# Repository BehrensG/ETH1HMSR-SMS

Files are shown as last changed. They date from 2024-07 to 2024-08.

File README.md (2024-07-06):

<h1>ETH1HMSR-SMS</h1>

ETH1HMSR-SMS is a one-channel data acquisition card based on the HMSR-SMS chip. The communication with a PC is over Ethernet. The card supports LAN eXtensions for Instrumentation (LXI) and RAW TCP and UDP connections.

<h2>DESCRIPTION</h2>

<h3>Device Design</h3>

Key features of the design include:

<ul>
    <li><b>Dimensions</b>: 100 x 45 mm</li>
    <li><b>Power Supply</b>: Operates on a voltage range from 6.5 to 36 VDC (recommended 24 VDC) and includes reverse voltage protection.</li>
    <li><b>Isolation</b>: The HMSR-SMS chip provides isolation protection for the rest of the circuit.</li>
    <li><b>MCU</b>: The STM32H743VITx was selected because of its large internal FLASH and RAM memory, support for Ethernet, and internal 16-bit ADC.</li>
    <li><b>ADC</b>: Internal 16 bit ADC, configured in differential mode.</li>
    <li><b>Software</b>: FreeRTOS with lwip and SCPI parser library.</li>
</ul>

<p align="center">3D model rendition for PCB V1.2.</p>
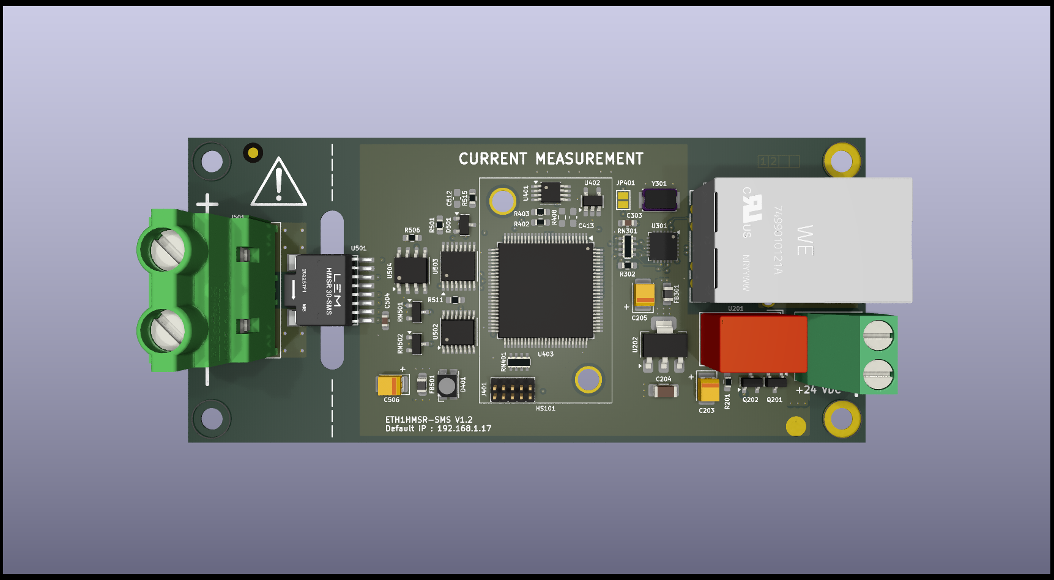
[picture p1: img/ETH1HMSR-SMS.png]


<p align="center">Below are the images for the PCB V1.0. I made some mistakes, but the botch wires fixed them.</p>

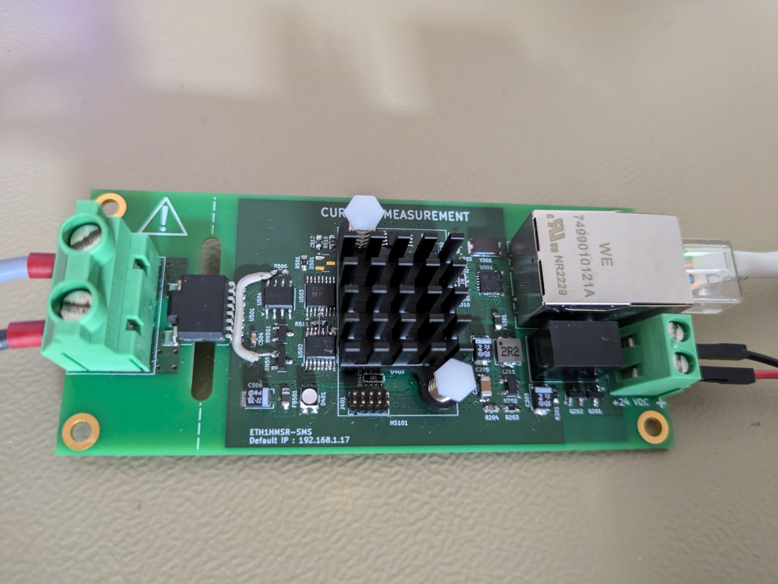
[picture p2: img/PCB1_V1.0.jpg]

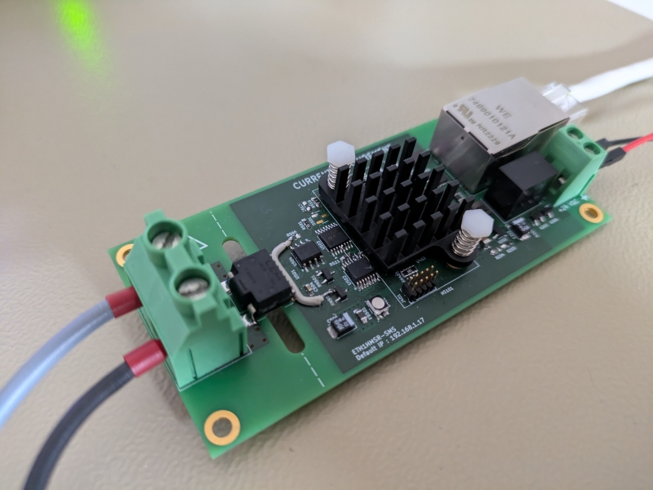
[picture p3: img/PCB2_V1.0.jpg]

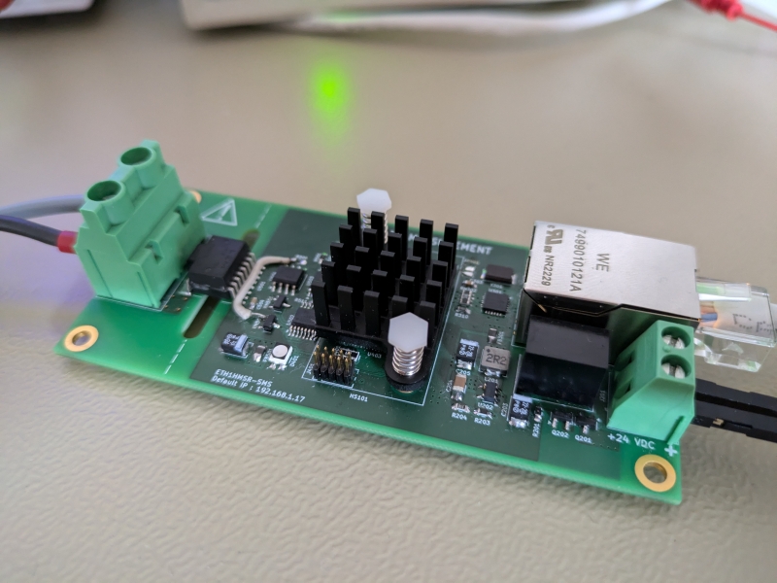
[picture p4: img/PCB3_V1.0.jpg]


<h3>Input current</h3>

The user can mount different HMSR-SMS models for different measurement ranges, those are :

<table align="center">
    <tr>
        <th>Model</th>
        <th>Nominal current (A)</th>
        <th>Measurement range (A)</th>
        <th>Supported</th>
    </tr>
    <tr>
        <td>HMSR6-SMS</td>
        <td>6</td>
        <td>+/- 15</td>
        <td><font color="green">YES</font></td>
    </tr>
    <tr>
        <td>HMSR8-SMS</td>
        <td>8</td>
        <td>+/- 20</td>
        <td><font color="green">YES</font></td>
    </tr>
    <tr>
        <td>HMSR10-SMS</td>
        <td>10</td>
        <td>+/- 25</td>
        <td><font color="green">YES</font></td>
    </tr>
    <tr>
        <td>HMSR15-SMS</td>
        <td>15</td>
        <td>+/- 37.5</td>
        <td><font color="green">YES</font></td>
    </tr>
    <tr>
        <td>HMSR20-SMS</td>
        <td>20</td>
        <td>+/- 50</td>
        <td><font color="red">NO</font></td>
    </tr>
    <tr>
        <td>HMSR30-SMS</td>
        <td>30</td>
        <td>+/- 75</td>
        <td><font color="red">NO</font></td>
    </tr>
</table>

> [!NOTE]
> The limitations is the input connector (Phoenix Contact 1710072), with nominal current of 32 A. For larger current models, the user need to redesign the PCB.

> [!NOTE]
> The prototype has a HMSR6-SMS. Other current models where not tested.

> [!TIP]
> The HMSR-SMS chip is accurate without any additional calibration.

<h2>Ethernet connection</h2>

The PCB uses Ethernet to communicate with the PC. The features are :

<h3>LAN eXtensions for Instrumentation (LXI)</h3>

LAN eXtensions for Instrumentation (LXI) is a standard for connecting and controlling test and measurement instruments via Ethernet. It allows for easy integration, remote access, and simplified configuration, enhancing the flexibility and scalability of automated test systems.

> [!WARNING]  
> This device does not guarantee full compliance with the LXI standard. The implementation was based on available documentation and observations of an LXI-compliant device.

> [!TIP]
> To use the LXI features the user needs to use a VISA API. In the examples below, the R&S VISA Tools where uses. 

<h4><p align="center">Device autodetect with multicast DNS (mDNS).</p></h4>
<hr>
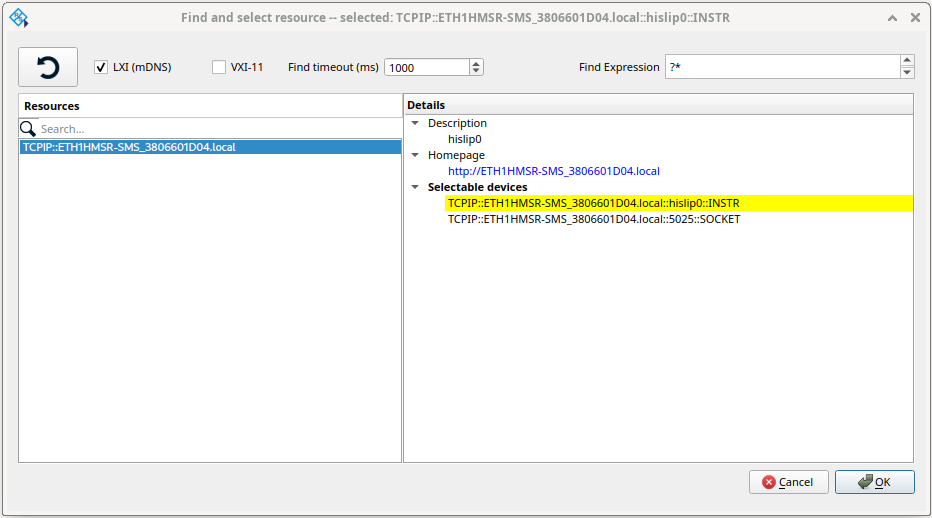
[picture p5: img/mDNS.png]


<h4><p align="center">Support for High Speed LAN Instrument Protocol (HiSLIP).</p></h4>
<hr>
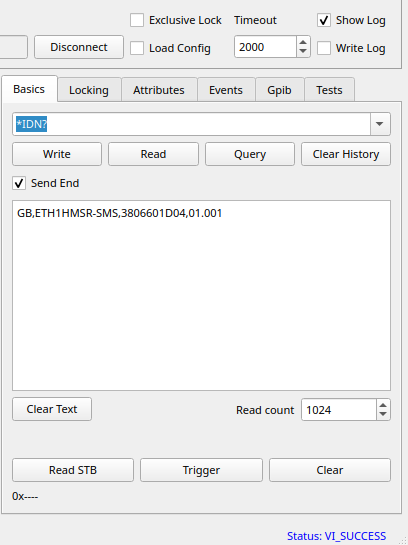
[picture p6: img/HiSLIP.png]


<h4><p align="center">Web interface</p></h4>
<hr>
The device website provides the ability to obtain device information, make measurements, and configure the device. Additionally, it offers a manual with all SCPI commands.

> [!WARNING]
> The website was tested only with Google Chrome  Browser.

<h5><p align="center">Device Home Page</p></h5>
<hr>
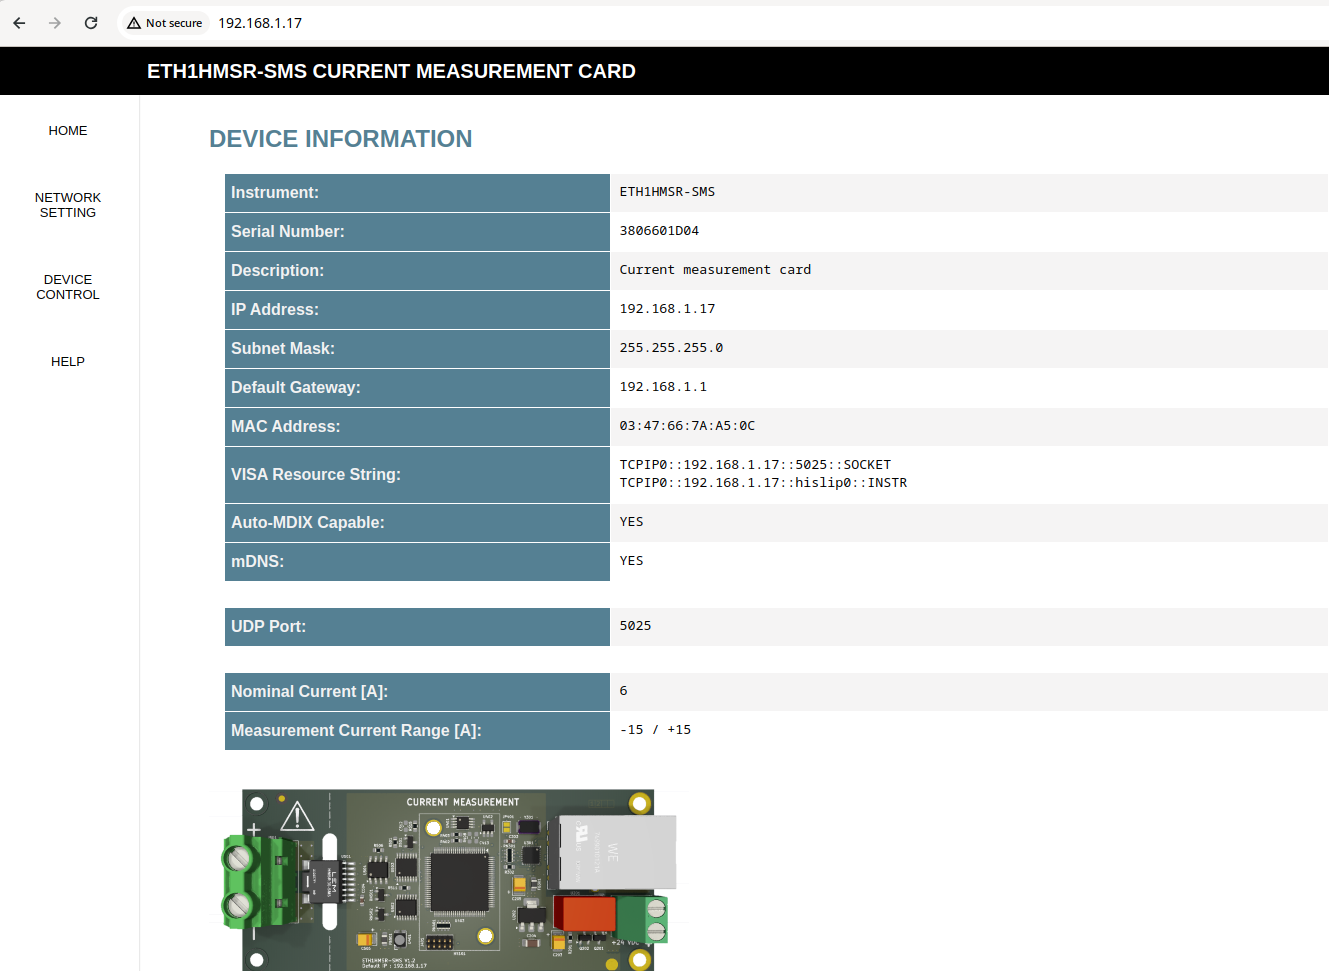
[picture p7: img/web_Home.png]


<h5><p align="center">Device Network Setup</p></h5>
<hr>
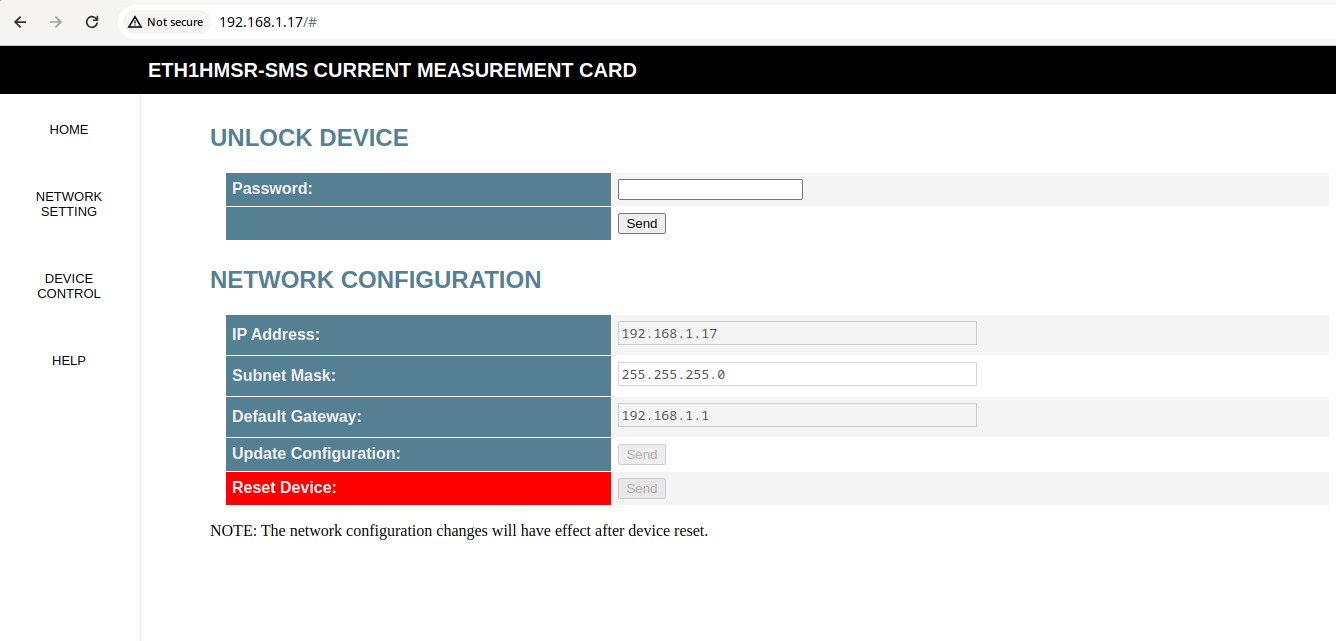
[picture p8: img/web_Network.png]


<h5><p align="center">Device Control</p></h5>
<hr>
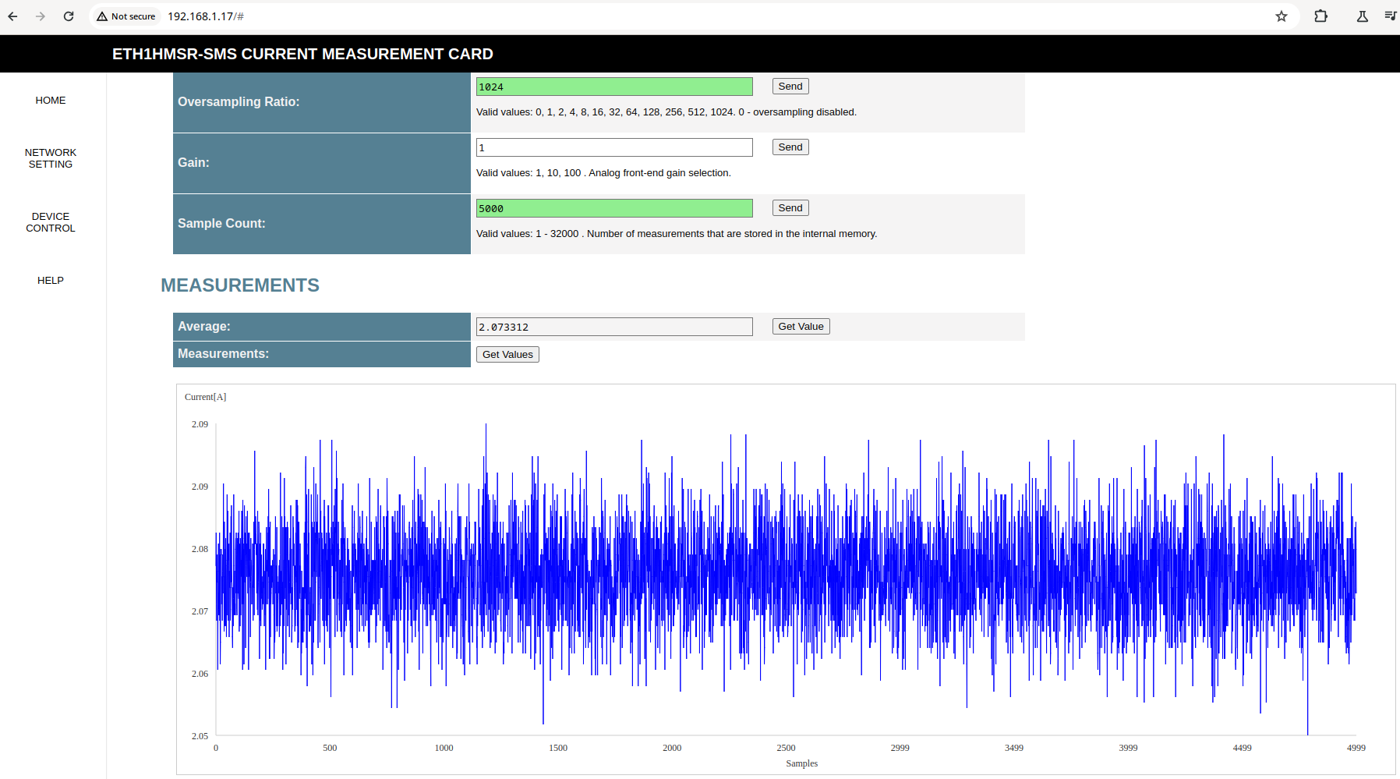
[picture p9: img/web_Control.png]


<h5><p align="center">Device Help</p></h5>
<hr>
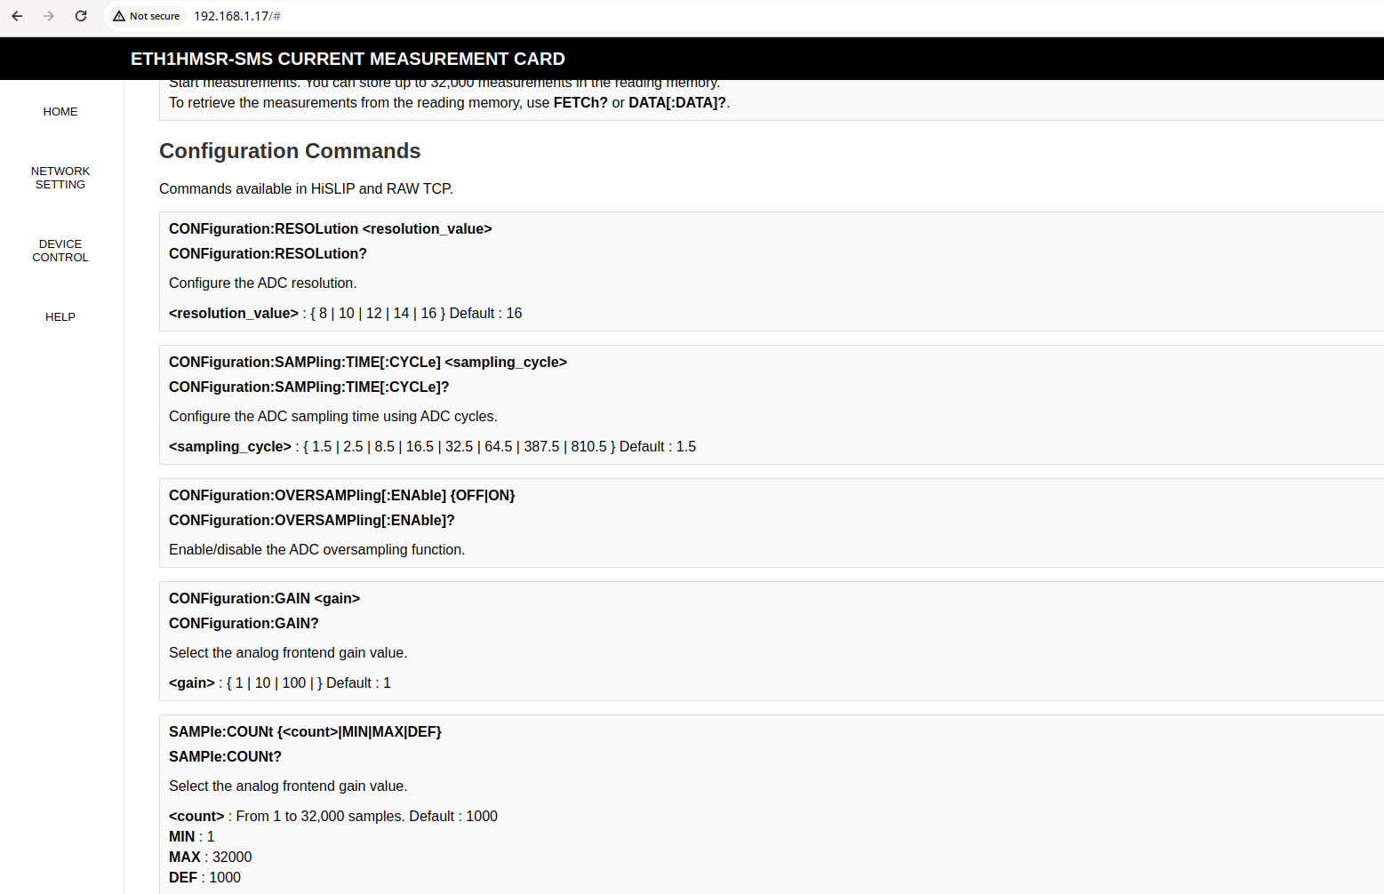
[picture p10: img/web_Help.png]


<h5><p align="center">Device Service</p></h5>
<hr>
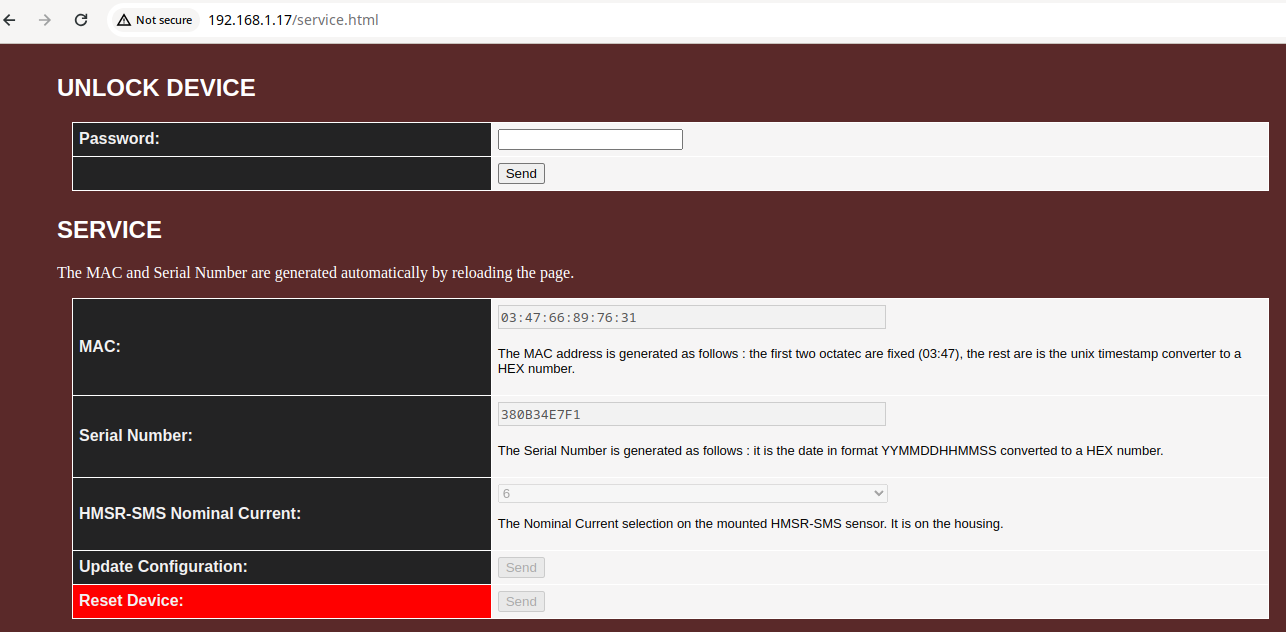
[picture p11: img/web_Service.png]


<h3>RAW TCP</h3>
The user can connect to the device directly over the TCP 5025 port.

<h5><p align="center">Using netcat</p></h5>
<hr>
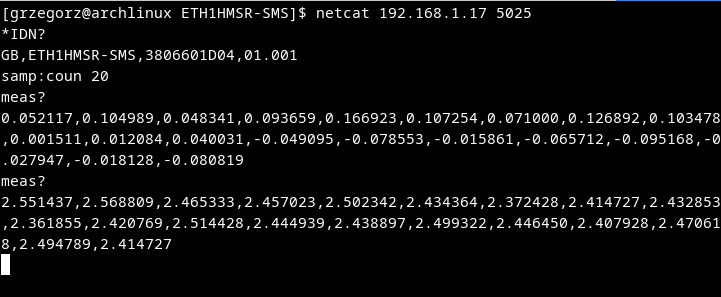
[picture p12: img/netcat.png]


<h5><p align="center">Using putty</p></h5>
<hr>
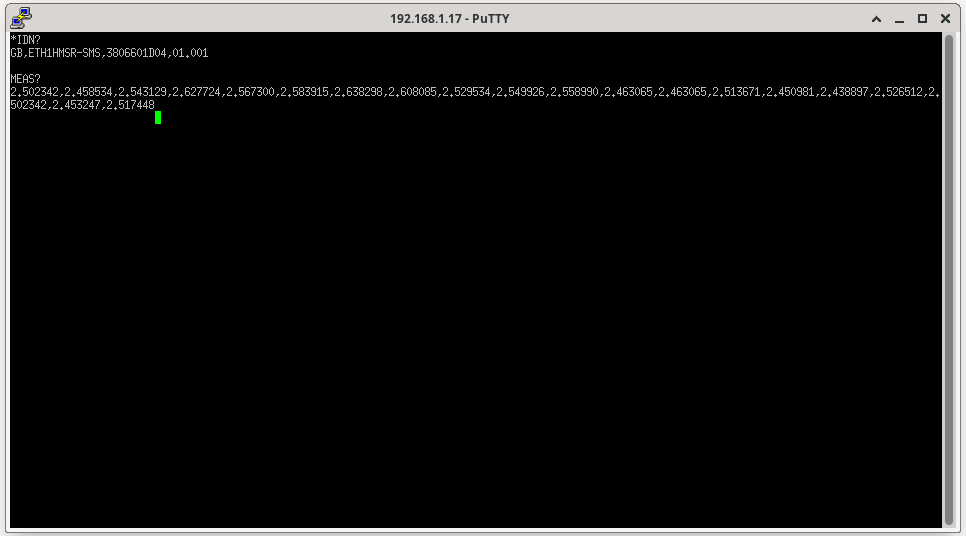
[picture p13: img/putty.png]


<h3>RAW UDP</h3>
The user can connect to the device directly via UDP port 5025. Over UDP, there is a very limited set of SCPI commands available for measurement readout.

> [!WARNING]
> The RAW UDP connection is not part of the LXI standard, it is device specific.

<h5><p align="center">Using netcat</p></h5>
<hr>
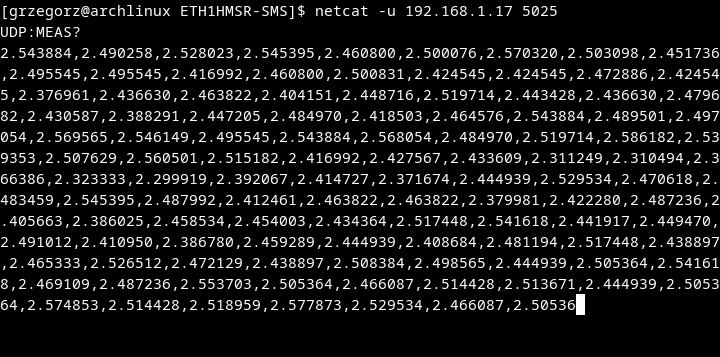
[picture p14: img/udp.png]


<h2>Links</h2>

<ul>
    <li><a href="https://www.lem.com/en/hmsr-series" target="_blank">HMSR-SMS</a></li>
    <li><a href="https://www.lxistandard.org/" target="_blank">LAN eXtensions for Instrumentation</a></li>
    <li><a href="https://www.ivifoundation.org/specifications/default.html" target="_blank">High Speed LAN Instrument Protocol (HiSLIP)</a></li>
    <li><a href="https://en.wikipedia.org/wiki/Virtual_instrument_software_architecture" target="_blank">Virtual instrument software architecture (VISA)</a></li>
    <li><a href="https://www.rohde-schwarz.com/us/driver-pages/remote-control/3-visa-and-tools_231388.html" target="_blank">R&S VISA</a></li>
    <li><a href="https://github.com/j123b567/scpi-parser" target="_blank">SCPI Parser</a></li>
   <li><a href="https://github.com/mpaland/printf" target="_blank">A printf / sprintf Implementation for Embedded Systems</a></li>
</ul>

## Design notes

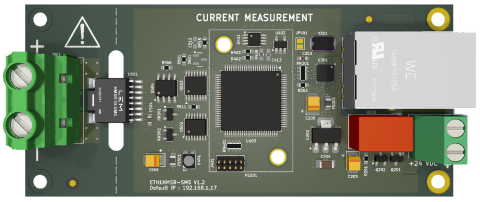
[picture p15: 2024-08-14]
SOFTWARE/ETH1HMSR-SMS/Core/BSP/HTTP/fs/img/instrument.png

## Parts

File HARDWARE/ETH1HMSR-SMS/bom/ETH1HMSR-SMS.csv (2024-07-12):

Id | Designator | Footprint | Quantity | Designation | Supplier and ref
1 | RN502,RN501 | SOT-23 | 2 | MPMT2003AT5
2 | U503 | TSSOP-16_4.4x5mm_P0.65mm | 1 | DG412LEDQ
3 | J201 | TerminalBlock_Phoenix_MKDS-1,5-2_1x02_P5.00mm_Horizontal | 1 | 1715721
4 | FB301,FB501,FB401 | L_0805_2012Metric_Pad1.05x1.20mm_HandSolder | 3 | 742792031
5 | D401 | LED_Avago_PLCC4_3.2x2.8mm_CW | 1 | ASMB-MTB1-0B3A2
6 | RN401 | R_Array_Concave_4x0603 | 1 | EXB-V8V102JV
7 | C204 | C_1206_3216Metric_Pad1.33x1.80mm_HandSolder | 1 | 10u
8 | J301 | RJ45_Wuerth_7499010121A_Horizontal | 1 | RJ45_Wuerth_7499010121A
9 | Q201 | SOT-23 | 1 | SI5618A
10 | C504,C503,C403,C505,C308,C410,C401,C501,C508,C409,C421,C407,C405,C502,C406,C312,C411,C507,C311,C309,C415,C404,C310,C422,C302 | C_0603_1608Metric_Pad1.08x0.95mm_HandSolder | 25 | 0.1u
11 | C506,C203,C205 | CP_EIA-3528-21_Kemet-B_Pad1.50x2.35mm_HandSolder | 3 | 22u
12 | R302 | R_0603_1608Metric_Pad0.98x0.95mm_HandSolder | 1 | 1k5
13 | U504 | SOIC-8_3.9x4.9mm_P1.27mm | 1 | DG419LEDY
14 | C303 | C_0603_1608Metric_Pad1.08x0.95mm_HandSolder | 1 | 470p
15 | Y301 | NX5032GA | 1 | NX5032GA-25
16 | J501 | 1710072 | 1 | 1710072
17 | J401 | PinHeader_2x05_P1.27mm_Vertical | 1 | 20021111-00010T4LF
18 | U403 | LQFP-100_14x14mm_P0.5mm | 1 | STM32H743VITx
19 | R403,R402,R506,R515,R405 | R_0603_1608Metric_Pad0.98x0.95mm_HandSolder | 5 | 0
20 | U301 | VQFN-24-1EP_4x4mm_P0.5mm_EP2.5x2.5mm_ThermalVias | 1 | LAN8742A
21 | U202 | SOT-223-3_TabPin2 | 1 | LM1117MP-3.3/NOPB
22 | HS101 | 960-19-12-S-AB-0 | 1 | 960-19-12-S-AB-0
23 | R201,R501,R202 | R_0603_1608Metric_Pad0.98x0.95mm_HandSolder | 3 | 100k
24 | U501 | HMSR-SMS | 1 | HMSR-SMS
25 | Q202 | SOT-23 | 1 | MMBT3904
26 | RN301 | R_Array_Concave_4x0603 | 1 | EXB-V8V330JV
27 | U401 | MSOP-8_3x3mm_P0.65mm | 1 | LT6350xMS8
28 | U402 | SOT-23-5_HandSoldering | 1 | REF2033AIDDCT
29 | R511 | R_0603_1608Metric_Pad0.98x0.95mm_HandSolder | 1 | 100k/0.1%
30 | U201 | Converter_DCDC_TRACO_TSR-1_THT | 1 | TSR_1-2450
31 | U502 | SSOP-16_3.9x4.9mm_P0.635mm | 1 | OPA4340EA
32 | C412,C305,C307,C408,C306,C414,C402 | C_0603_1608Metric_Pad1.08x0.95mm_HandSolder | 7 | 1u
33 | C201 | C_1206_3216Metric_Pad1.33x1.80mm_HandSolder | 1 | 10u/50V
34 | R407,R406 | R_0603_1608Metric_Pad0.98x0.95mm_HandSolder | 2 | 4k7
35 | C202 | C_1206_3216Metric_Pad1.33x1.80mm_HandSolder | 1 | 4u7/50V
36 | R303,R505,R502,R401,R504,R301,R404 | R_0603_1608Metric_Pad0.98x0.95mm_HandSolder | 7 | 10k
37 | C418 | C_0603_1608Metric_Pad1.08x0.95mm_HandSolder | 1 | 10u
38 | RN303 | R_Array_Concave_4x0603 | 1 | EXB-38V510JV
39 | R305,R306 | R_0603_1608Metric_Pad0.98x0.95mm_HandSolder | 2 | 560
40 | Y401 | NX5032GA | 1 | NX5032GA-16
41 | R513 | R_0603_1608Metric_Pad0.98x0.95mm_HandSolder | 1 | 18k/0.05%
42 | D202 | D_SOD-123 | 1 | 1N4148W
43 | C510,C511,C509 | C_0603_1608Metric_Pad1.08x0.95mm_HandSolder | 3 | 4n7
44 | D201 | SOT-23 | 1 | BZX84C10LT1G
45 | C416,C304,C301,C417 | C_0603_1608Metric_Pad1.08x0.95mm_HandSolder | 4 | 8p
46 | C419,C420 | C_0603_1608Metric_Pad1.08x0.95mm_HandSolder | 2 | 2u2
47 | U404 | MSOP-8_3x3mm_P0.65mm | 1 | 24LC08B-E/MS
48 | R512 | R_0603_1608Metric_Pad0.98x0.95mm_HandSolder | 1 | 180k/0.05%
49 | R514 | R_0603_1608Metric_Pad0.98x0.95mm_HandSolder | 1 | 2k/0.05%
50 | R503 | R_0603_1608Metric_Pad0.98x0.95mm_HandSolder | 1 | 30k
51 | R304 | R_0603_1608Metric_Pad0.98x0.95mm_HandSolder | 1 | 12k1
52 | RN302 | R_Array_Concave_4x0603 | 1 | EXB-V8V103JV
53 | F201 | Fuse_1812_4532Metric_Pad1.30x3.40mm_HandSolder | 1 | 1812L075/33DR

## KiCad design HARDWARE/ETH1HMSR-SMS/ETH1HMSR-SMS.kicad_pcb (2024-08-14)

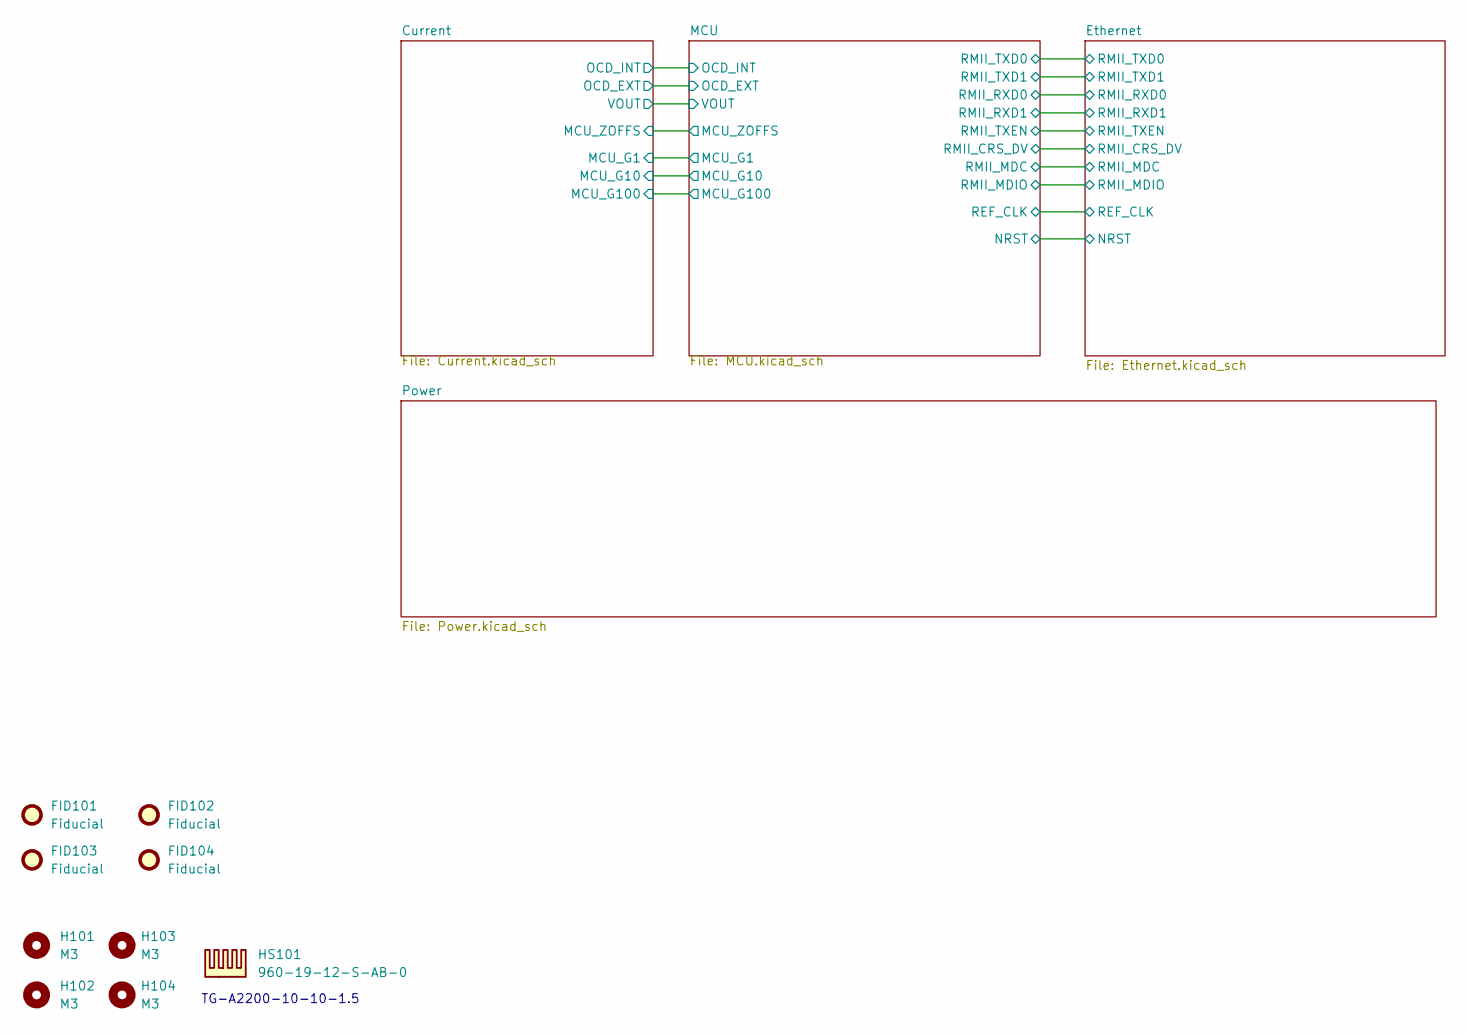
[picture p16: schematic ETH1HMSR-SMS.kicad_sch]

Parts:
FID101, FID102, FID103, FID104: Fiducial; Fiducial_1.5mm_Mask3mm
H101, H102: M3; MountingHole_3.2mm_M3_DIN965
H103, H104: M3; MountingHole_3.2mm_M3_DIN965_Pad
HS101: 960-19-12-S-AB-0

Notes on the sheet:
TG-A2200-10-10-1.5

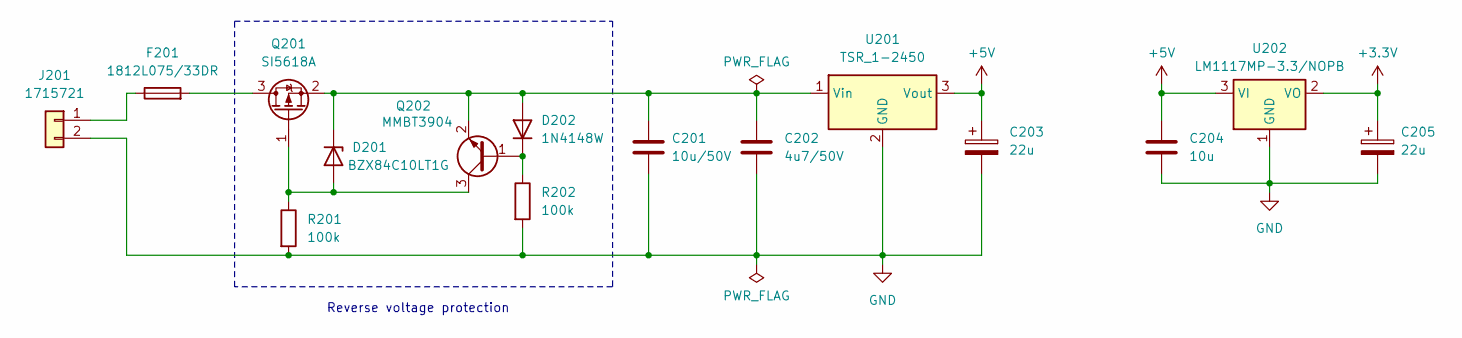
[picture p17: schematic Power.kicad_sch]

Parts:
C201: 10u/50V; C_1206_3216Metric_Pad1.33x1.80mm_HandSolder
C202: 4u7/50V; C_1206_3216Metric_Pad1.33x1.80mm_HandSolder
C203, C205: 22u; CP_EIA-3528-21_Kemet-B_Pad1.50x2.35mm_HandSolder
C204: 10u; C_1206_3216Metric_Pad1.33x1.80mm_HandSolder
D201: BZX84C10LT1G; SOT-23
D202: 1N4148W; D_SOD-123
F201: 1812L075/33DR; Fuse_1812_4532Metric_Pad1.30x3.40mm_HandSolder
J201: 1715721; TerminalBlock_Phoenix_MKDS-1,5-2_1x02_P5.00mm_Horizontal
Q201: SI5618A; SOT-23
Q202: MMBT3904; SOT-23
R201, R202: 100k; R_0603_1608Metric_Pad0.98x0.95mm_HandSolder
U201: TSR_1-2450; Converter_DCDC_TRACO_TSR-1_THT
U202: LM1117MP-3.3/NOPB; SOT-223-3_TabPin2

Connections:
+3.3V: C205.1, U202.2 (VO); also elsewhere on the board
+5V: C203.1, C204.1, U201.3 (Vout), U202.3 (VI); also elsewhere on the board
GND: C201.2, C202.2, C203.2, C204.2, C205.2, J201.2, R201.2, R202.2, U201.2 (GND), U202.1 (GND); also elsewhere on the board
unnamed: D201.1 (A), Q201.1 (G), Q202.3 (C), R201.1
unnamed: C201.1, C202.1, D201.3 (K), D202.2 (A), Q201.2 (S), Q202.2 (E), U201.1 (Vin)
unnamed: D202.1 (K), Q202.1 (B), R202.1
unnamed: F201.1, J201.1
unnamed: F201.2, Q201.3 (D)

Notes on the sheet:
Reverse voltage protection

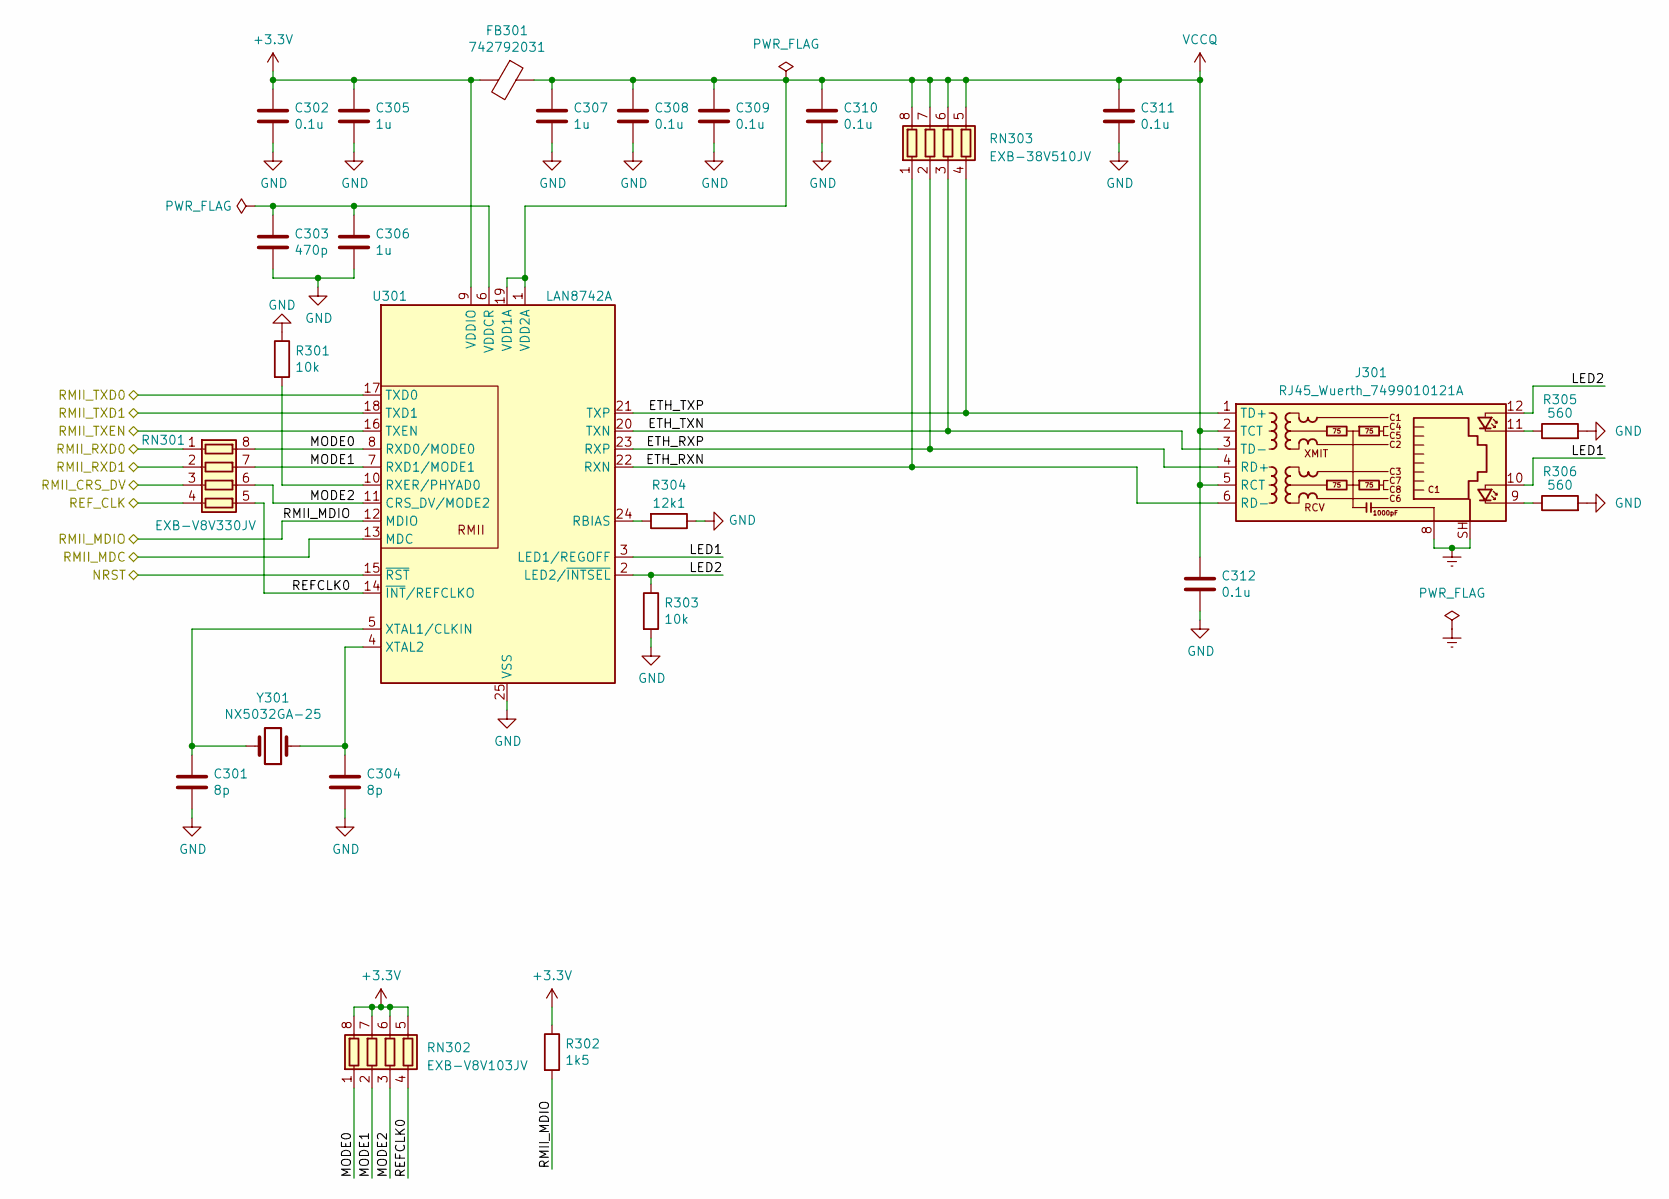
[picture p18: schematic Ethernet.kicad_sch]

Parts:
C301, C304: 8p; C_0603_1608Metric_Pad1.08x0.95mm_HandSolder
C302, C308, C309, C310, C311, C312: 0.1u; C_0603_1608Metric_Pad1.08x0.95mm_HandSolder
C303: 470p; C_0603_1608Metric_Pad1.08x0.95mm_HandSolder
C305, C306, C307: 1u; C_0603_1608Metric_Pad1.08x0.95mm_HandSolder
FB301: 742792031; L_0805_2012Metric_Pad1.05x1.20mm_HandSolder
J301: RJ45_Wuerth_7499010121A; RJ45_Wuerth_7499010121A_Horizontal
R301, R303: 10k; R_0603_1608Metric_Pad0.98x0.95mm_HandSolder
R302: 1k5; R_0603_1608Metric_Pad0.98x0.95mm_HandSolder
R304: 12k1; R_0603_1608Metric_Pad0.98x0.95mm_HandSolder
R305, R306: 560; R_0603_1608Metric_Pad0.98x0.95mm_HandSolder
RN301: EXB-V8V330JV; R_Array_Concave_4x0603
RN302: EXB-V8V103JV; R_Array_Concave_4x0603
RN303: EXB-38V510JV; R_Array_Concave_4x0603
U301: LAN8742A; VQFN-24-1EP_4x4mm_P0.5mm_EP2.5x2.5mm_ThermalVias
Y301: NX5032GA-25; NX5032GA

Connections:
+3.3V: C302.1, C305.1, FB301.2, R302.1, RN302.5 (R4.2), RN302.6 (R3.2), RN302.7 (R2.2), RN302.8 (R1.2), U301.9 (VDDIO); also elsewhere on the board
/Ethernet/ETH_RXN: J301.6 (RD-), RN303.1 (R1.1), U301.22 (RXN)
/Ethernet/ETH_RXP: J301.4 (RD+), RN303.2 (R2.1), U301.23 (RXP)
/Ethernet/ETH_TXN: J301.3 (TD-), RN303.3 (R3.1), U301.20 (TXN)
/Ethernet/ETH_TXP: J301.1 (TD+), RN303.4 (R4.1), U301.21 (TXP)
/Ethernet/LED1: J301.10, U301.3 (LED1/REGOFF)
/Ethernet/LED2: J301.12, R303.1, U301.2 (LED2/~INTSEL)
/Ethernet/MODE0: RN301.8 (R1.2), RN302.1 (R1.1), U301.8 (RXD0/MODE0)
/Ethernet/MODE1: RN301.7 (R2.2), RN302.2 (R2.1), U301.7 (RXD1/MODE1)
/Ethernet/MODE2: RN301.6 (R3.2), RN302.3 (R3.1), U301.11 (CRS_DV/MODE2)
/Ethernet/REFCLK0: RN301.5 (R4.2), RN302.4 (R4.1), U301.14 (~INT/REFCLKO)
/Ethernet/REF_CLK: RN301.4 (R4.1); also elsewhere on the board
/Ethernet/RMII_CRS_DV: RN301.3 (R3.1); also elsewhere on the board
/Ethernet/RMII_MDC: U301.13 (MDC); also elsewhere on the board
/Ethernet/RMII_MDIO: R302.2, U301.12 (MDIO); also elsewhere on the board
/Ethernet/RMII_RXD0: RN301.1 (R1.1); also elsewhere on the board
/Ethernet/RMII_RXD1: RN301.2 (R2.1); also elsewhere on the board
/Ethernet/RMII_TXD0: U301.17 (TXD0); also elsewhere on the board
/Ethernet/RMII_TXD1: U301.18 (TXD1); also elsewhere on the board
/Ethernet/RMII_TXEN: U301.16 (TXEN); also elsewhere on the board
/MCU/NRST: U301.15 (~RST); also elsewhere on the board
Earth: J301.8, J301.SH
GND: C301.2, C302.2, C303.2, C304.2, C305.2, C306.2, C307.2, C308.2, C309.2, C310.2, C311.2, C312.2, R301.1, R303.2, R304.1, R305.2, R306.2, U301.25 (VSS); also elsewhere on the board
unnamed: J301.9, R306.1
unnamed: J301.11, R305.1
unnamed: R304.2, U301.24 (RBIAS)
unnamed: R301.2, U301.10 (RXER/PHYAD0)
unnamed: C303.1, C306.1, U301.6 (VDDCR)
unnamed: C301.1, U301.5 (XTAL1/CLKIN), Y301.2
unnamed: C304.1, U301.4 (XTAL2), Y301.1
VCCQ: C307.1, C308.1, C309.1, C310.1, C311.1, C312.1, FB301.1, J301.2 (TCT), J301.5 (RCT), RN303.5 (R4.2), RN303.6 (R3.2), RN303.7 (R2.2), RN303.8 (R1.2), U301.1 (VDD2A), U301.19 (VDD1A)

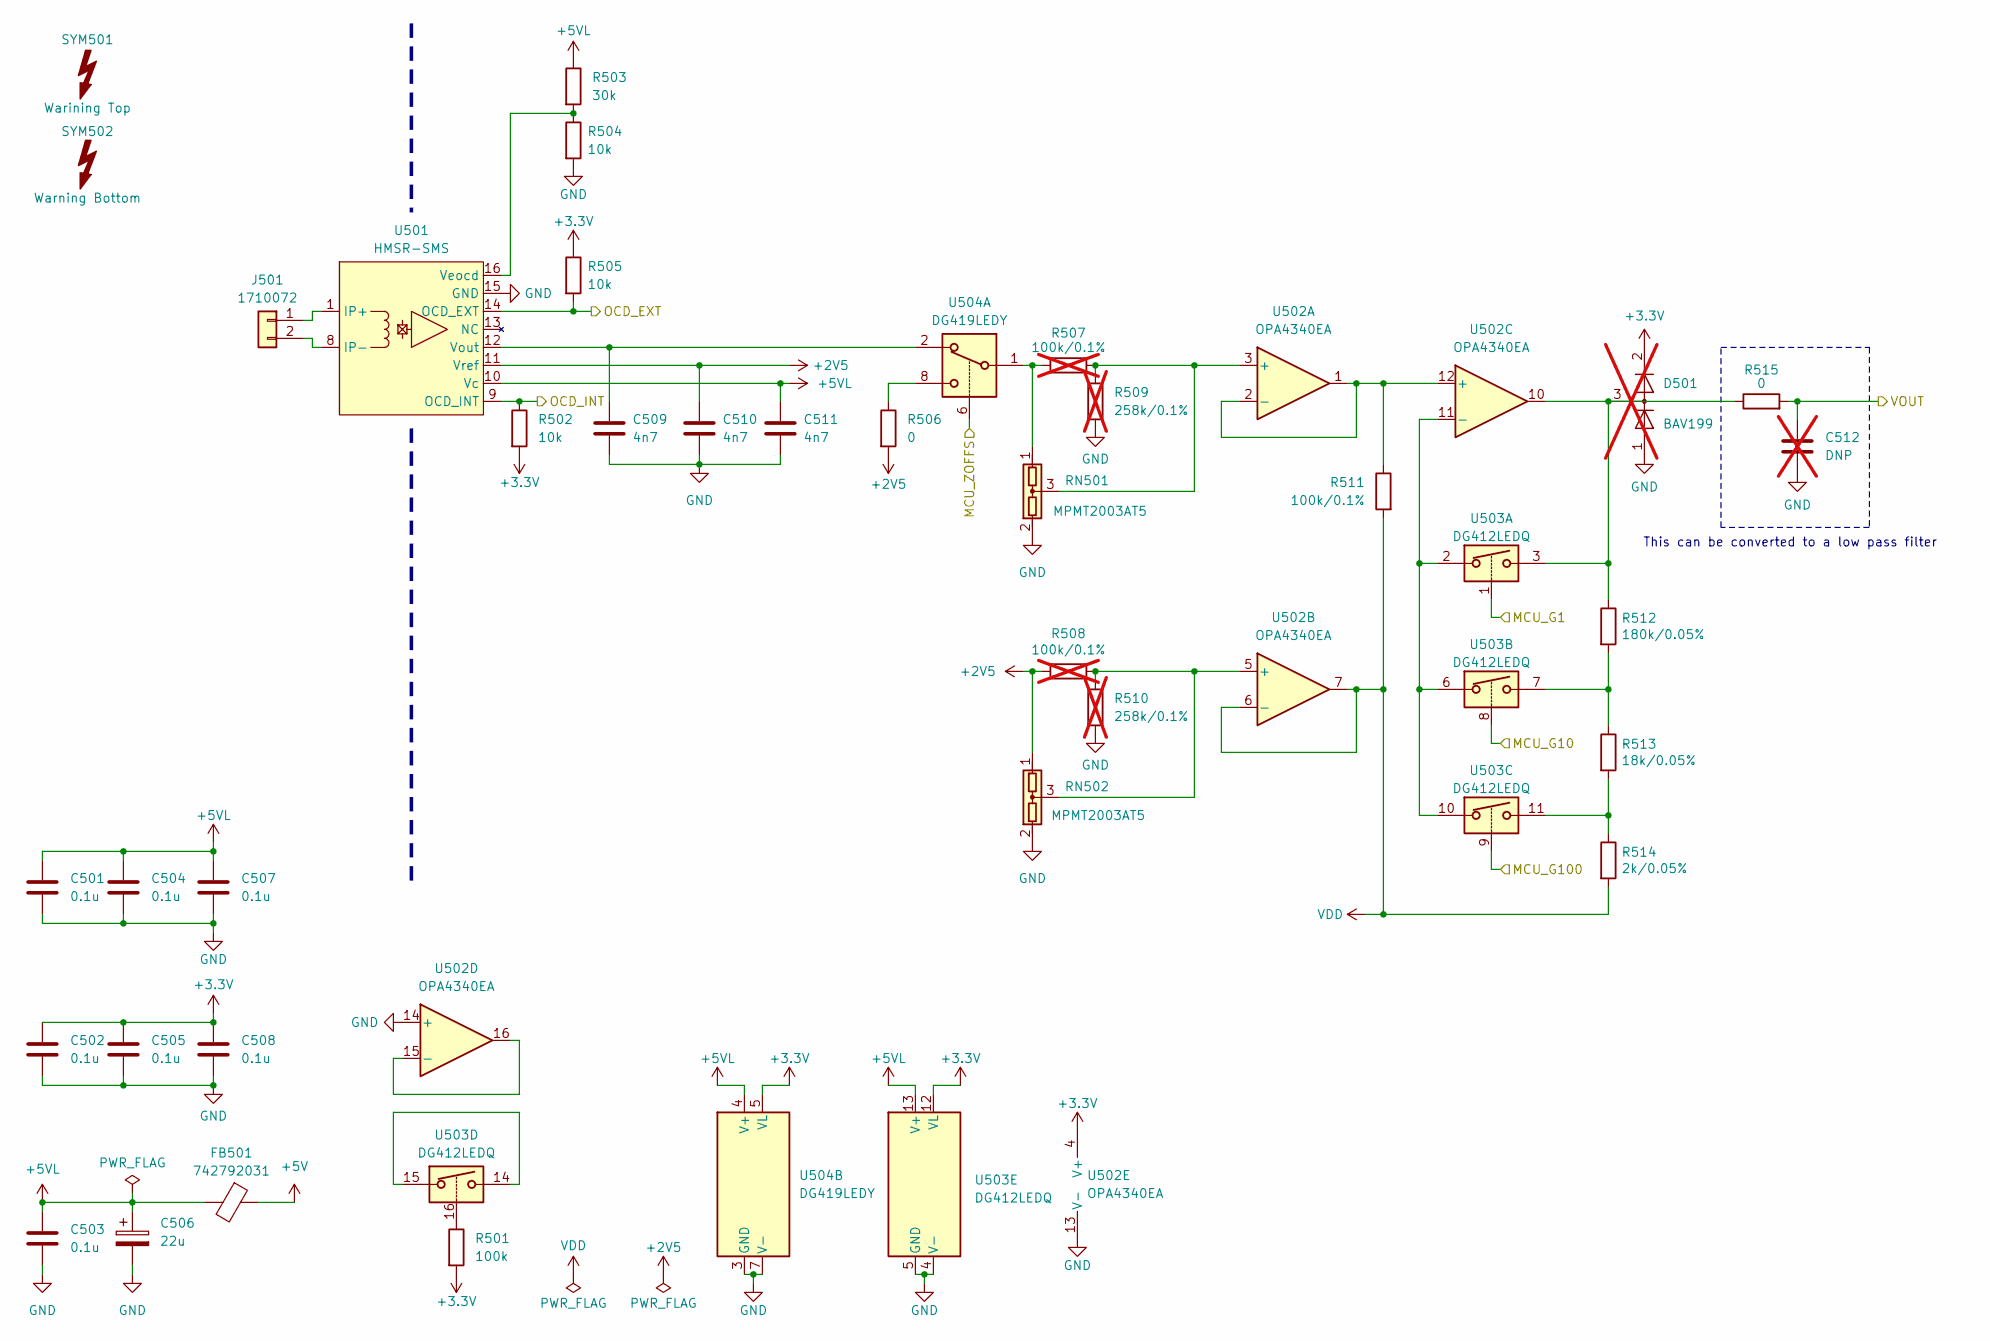
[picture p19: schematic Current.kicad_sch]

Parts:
C501, C502, C503, C504, C505, C507, C508: 0.1u; C_0603_1608Metric_Pad1.08x0.95mm_HandSolder
C506: 22u; CP_EIA-3528-21_Kemet-B_Pad1.50x2.35mm_HandSolder
C509, C510, C511: 4n7; C_0603_1608Metric_Pad1.08x0.95mm_HandSolder
C512: DNP; C_0603_1608Metric_Pad1.08x0.95mm_HandSolder; not fitted
D501: BAV199; SOT-23; not fitted
FB501: 742792031; L_0805_2012Metric_Pad1.05x1.20mm_HandSolder
J501: 1710072
R501: 100k; R_0603_1608Metric_Pad0.98x0.95mm_HandSolder
R502, R504, R505: 10k; R_0603_1608Metric_Pad0.98x0.95mm_HandSolder
R503: 30k; R_0603_1608Metric_Pad0.98x0.95mm_HandSolder
R506, R515: 0; R_0603_1608Metric_Pad0.98x0.95mm_HandSolder
R507, R508: 100k/0.1%; R_0603_1608Metric_Pad0.98x0.95mm_HandSolder; not fitted
R509, R510: 258k/0.1%; R_0603_1608Metric_Pad0.98x0.95mm_HandSolder; not fitted
R511: 100k/0.1%; R_0603_1608Metric_Pad0.98x0.95mm_HandSolder
R512: 180k/0.05%; R_0603_1608Metric_Pad0.98x0.95mm_HandSolder
R513: 18k/0.05%; R_0603_1608Metric_Pad0.98x0.95mm_HandSolder
R514: 2k/0.05%; R_0603_1608Metric_Pad0.98x0.95mm_HandSolder
RN501, RN502: MPMT2003AT5; SOT-23
SYM501: Warining Top; Symbol_Attention_Triangle_8x7mm_Copper
SYM502: Warning Bottom; Symbol_Attention_Triangle_8x7mm_Copper
U501: HMSR-SMS
U502: OPA4340EA; SSOP-16_3.9x4.9mm_P0.635mm
U503: DG412LEDQ; TSSOP-16_4.4x5mm_P0.65mm
U504: DG419LEDY; SOIC-8_3.9x4.9mm_P1.27mm

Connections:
+2V5: C510.1, R506.2, R508.1, RN502.1, U501.11 (Vref)
+3.3V: C502.1, C505.1, C508.1, D501.2 (A), R501.2, R502.2, R505.1, U502.4 (V+), U503.12 (VL), U504.5 (VL); also elsewhere on the board
+5V: FB501.1; also elsewhere on the board
+5VL: C501.1, C503.1, C504.1, C506.1, C507.1, C511.1, FB501.2, R503.1, U501.10 (Vc), U503.13 (V+), U504.4 (V+); also elsewhere on the board
/Current/MCU_G1: U503.1; also elsewhere on the board
/Current/MCU_G10: U503.8; also elsewhere on the board
/Current/MCU_G100: U503.9; also elsewhere on the board
/Current/MCU_ZOFFS: U504.6; also elsewhere on the board
/Current/OCD_EXT: R505.2, U501.14 (OCD_EXT); also elsewhere on the board
/Current/OCD_INT: R502.1, U501.9 (OCD_INT); also elsewhere on the board
/Current/VOUT: C512.1, R515.2; also elsewhere on the board
GND: C501.2, C502.2, C503.2, C504.2, C505.2, C506.2, C507.2, C508.2, C509.2, C510.2, C511.2, C512.2, D501.1 (K), R504.2, R509.2, R510.2, RN501.2, RN502.2, U501.15 (GND), U502.13 (V-), U502.14 (+), U503.4 (V-), U503.5 (GND), U504.3 (GND), U504.7 (V-); also elsewhere on the board
unnamed: D501.3 (K), R512.1, R515.1, U502.10, U503.3
unnamed: J501.1, U501.1 (IP+)
unnamed: J501.2, U501.8 (IP-)
unnamed: R501.1, U503.16
unnamed: R506.1, U504.8
unnamed: R507.1, RN501.1, U504.1
unnamed: R512.2, R513.1, U503.7
unnamed: R513.2, R514.1, U503.11
unnamed: R503.2, R504.1, U501.16 (Veocd)
unnamed: C509.1, U501.12 (Vout), U504.2
unnamed: R507.2, R509.1, RN501.3, U502.3 (+)
unnamed: R511.1, U502.1, U502.2 (-), U502.12 (+)
unnamed: R508.2, R510.1, RN502.3, U502.5 (+)
unnamed: U502.11 (-), U503.2, U503.6, U503.10
unnamed: U502.15 (-), U502.16
unnamed: U503.14, U503.15
VDD: R511.2, R514.2, U502.6 (-), U502.7; also elsewhere on the board

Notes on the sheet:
This can be converted to a low pass filter

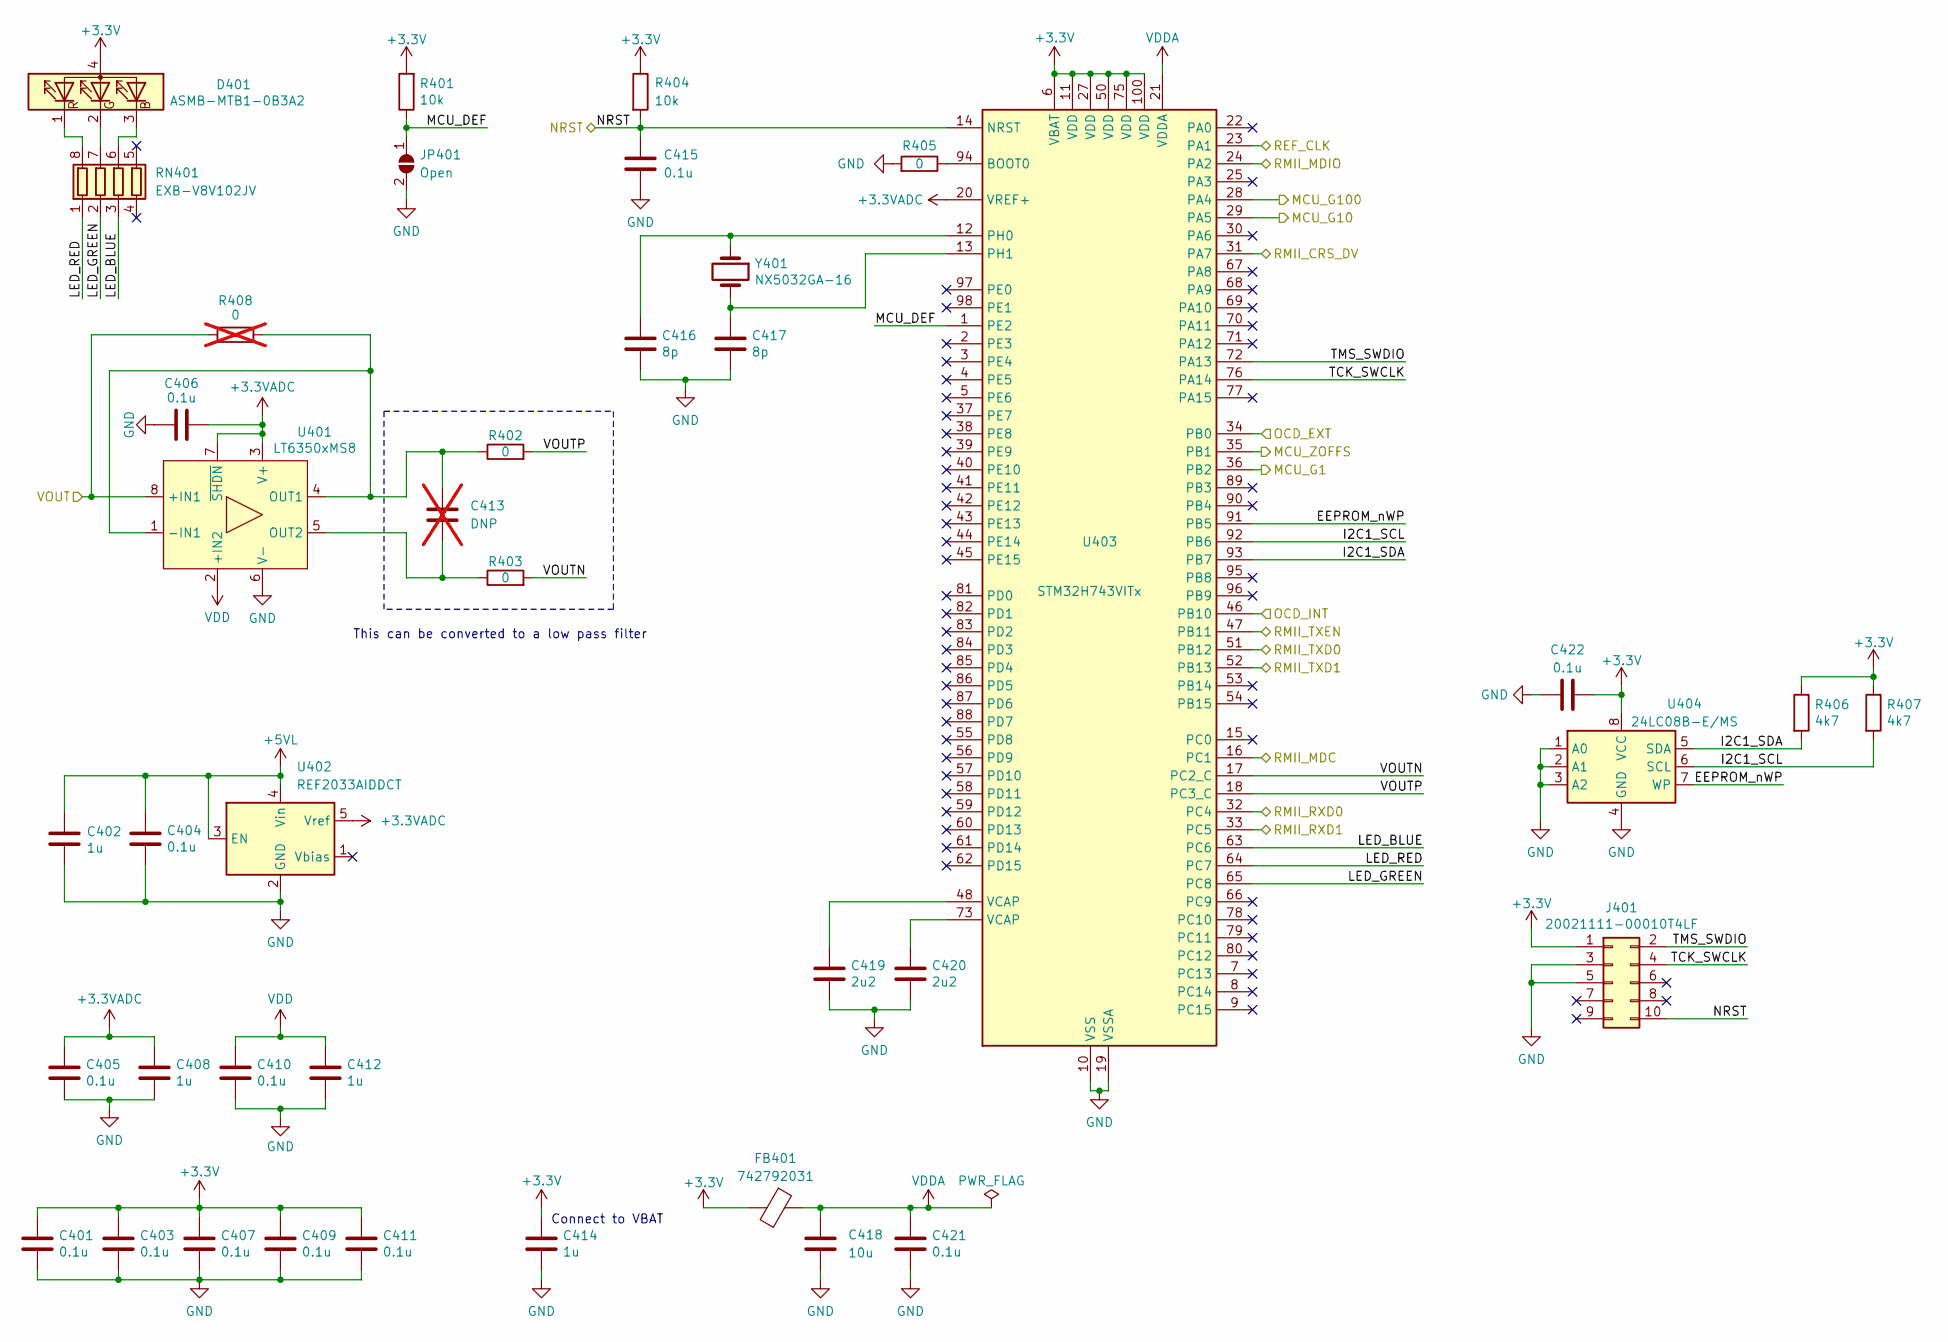
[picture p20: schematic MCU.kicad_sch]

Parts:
C401, C403, C404, C405, C406, C407, C409, C410, C411, C415, C421, C422: 0.1u; C_0603_1608Metric_Pad1.08x0.95mm_HandSolder
C402, C408, C412, C414: 1u; C_0603_1608Metric_Pad1.08x0.95mm_HandSolder
C413: DNP; C_0603_1608Metric_Pad1.08x0.95mm_HandSolder; not fitted
C416, C417: 8p; C_0603_1608Metric_Pad1.08x0.95mm_HandSolder
C418: 10u; C_0603_1608Metric_Pad1.08x0.95mm_HandSolder
C419, C420: 2u2; C_0603_1608Metric_Pad1.08x0.95mm_HandSolder
D401: ASMB-MTB1-0B3A2; LED_Avago_PLCC4_3.2x2.8mm_CW
FB401: 742792031; L_0805_2012Metric_Pad1.05x1.20mm_HandSolder
J401: 20021111-00010T4LF; PinHeader_2x05_P1.27mm_Vertical
JP401: Open; SolderJumper-2_P1.3mm_Open_Pad1.0x1.5mm
R401, R404: 10k; R_0603_1608Metric_Pad0.98x0.95mm_HandSolder
R402, R403, R405: 0; R_0603_1608Metric_Pad0.98x0.95mm_HandSolder
R406, R407: 4k7; R_0603_1608Metric_Pad0.98x0.95mm_HandSolder
R408: 0; R_0603_1608Metric_Pad0.98x0.95mm_HandSolder; not fitted
RN401: EXB-V8V102JV; R_Array_Concave_4x0603
U401: LT6350xMS8; MSOP-8_3x3mm_P0.65mm
U402: REF2033AIDDCT; SOT-23-5_HandSoldering
U403: STM32H743VITx; LQFP-100_14x14mm_P0.5mm
U404: 24LC08B-E/MS; MSOP-8_3x3mm_P0.65mm
Y401: NX5032GA-16; NX5032GA

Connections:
+3.3V: C401.1, C403.1, C407.1, C409.1, C411.1, C414.1, C422.2, D401.4 (A), FB401.2, J401.1, R401.2, R404.1, R406.1, R407.1, U403.6 (VBAT), U403.11 (VDD), U403.27 (VDD), U403.50 (VDD), U403.75 (VDD), U403.100 (VDD), U404.8 (VCC); also elsewhere on the board
+3.3VADC: C405.1, C406.1, C408.1, U401.3 (V+), U401.7 (~SHDN), U402.5 (Vref), U403.20 (VREF+)
+5VL: C402.1, C404.1, U402.3 (EN), U402.4 (Vin); also elsewhere on the board
/Current/MCU_G1: U403.36 (PB2); also elsewhere on the board
/Current/MCU_G10: U403.29 (PA5); also elsewhere on the board
/Current/MCU_G100: U403.28 (PA4); also elsewhere on the board
/Current/MCU_ZOFFS: U403.35 (PB1); also elsewhere on the board
/Current/OCD_EXT: U403.34 (PB0); also elsewhere on the board
/Current/OCD_INT: U403.46 (PB10); also elsewhere on the board
/Current/VOUT: R408.1, U401.8 (+IN1); also elsewhere on the board
/Ethernet/REF_CLK: U403.23 (PA1); also elsewhere on the board
/Ethernet/RMII_CRS_DV: U403.31 (PA7); also elsewhere on the board
/Ethernet/RMII_MDC: U403.16 (PC1); also elsewhere on the board
/Ethernet/RMII_MDIO: U403.24 (PA2); also elsewhere on the board
/Ethernet/RMII_RXD0: U403.32 (PC4); also elsewhere on the board
/Ethernet/RMII_RXD1: U403.33 (PC5); also elsewhere on the board
/Ethernet/RMII_TXD0: U403.51 (PB12); also elsewhere on the board
/Ethernet/RMII_TXD1: U403.52 (PB13); also elsewhere on the board
/Ethernet/RMII_TXEN: U403.47 (PB11); also elsewhere on the board
/MCU/EEPROM_nWP: U403.91 (PB5), U404.7 (WP)
/MCU/I2C1_SCL: R407.2, U403.92 (PB6), U404.6 (SCL)
/MCU/I2C1_SDA: R406.2, U403.93 (PB7), U404.5 (SDA)
/MCU/LED_BLUE: RN401.3 (R3.1), U403.63 (PC6)
/MCU/LED_GREEN: RN401.2 (R2.1), U403.65 (PC8)
/MCU/LED_RED: RN401.1 (R1.1), U403.64 (PC7)
/MCU/MCU_DEF: JP401.1 (A), R401.1, U403.1 (PE2)
/MCU/NRST: C415.1, J401.10, R404.2, U403.14 (NRST); also elsewhere on the board
/MCU/TCK_SWCLK: J401.4, U403.76 (PA14)
/MCU/TMS_SWDIO: J401.2, U403.72 (PA13)
/MCU/VOUTN: R403.2, U403.17 (PC2_C)
/MCU/VOUTP: R402.2, U403.18 (PC3_C)
GND: C401.2, C402.2, C403.2, C404.2, C405.2, C406.2, C407.2, C408.2, C409.2, C410.2, C411.2, C412.2, C414.2, C415.2, C416.2, C417.2, C418.2, C419.2, C420.2, C421.2, C422.1, J401.3, J401.5, JP401.2 (B), R405.2, U401.6 (V-), U402.2 (GND), U403.10 (VSS), U403.19 (VSSA), U403.26 (VSS), U403.49 (VSS), U403.74 (VSS), U403.99 (VSS), U404.1 (A0), U404.2 (A1), U404.3 (A2), U404.4 (GND); also elsewhere on the board
unnamed: C419.1, U403.48 (VCAP)
unnamed: C420.1, U403.73 (VCAP)
unnamed: D401.3 (BK), RN401.6 (R3.2)
unnamed: D401.2 (GK), RN401.7 (R2.2)
unnamed: D401.1 (RK), RN401.8 (R1.2)
unnamed: C413.1, R402.1, R408.2, U401.1 (-IN1), U401.4 (OUT1)
unnamed: C413.2, R403.1, U401.5 (OUT2)
unnamed: R405.1, U403.94 (BOOT0)
unnamed: C416.1, U403.12 (PH0), Y401.1
unnamed: C417.1, U403.13 (PH1), Y401.2
VDD: C410.1, C412.1, U401.2 (+IN2); also elsewhere on the board
VDDA: C418.1, C421.1, FB401.1, U403.21 (VDDA)

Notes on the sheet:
This can be converted to a low pass filter
Connect to VBAT

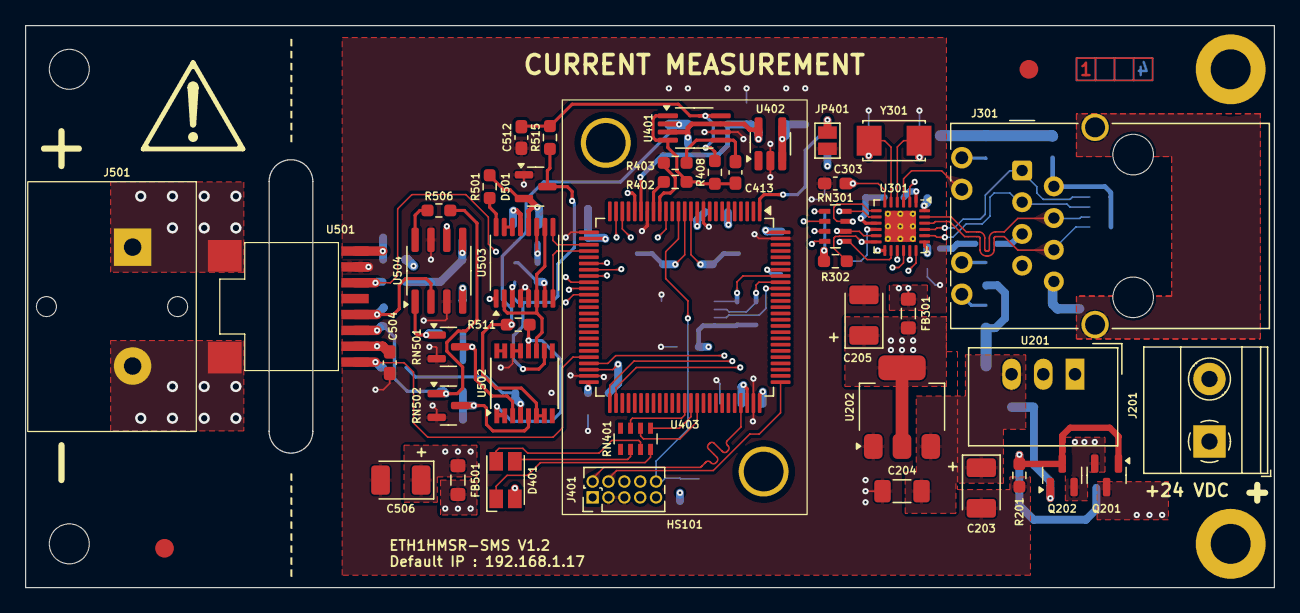
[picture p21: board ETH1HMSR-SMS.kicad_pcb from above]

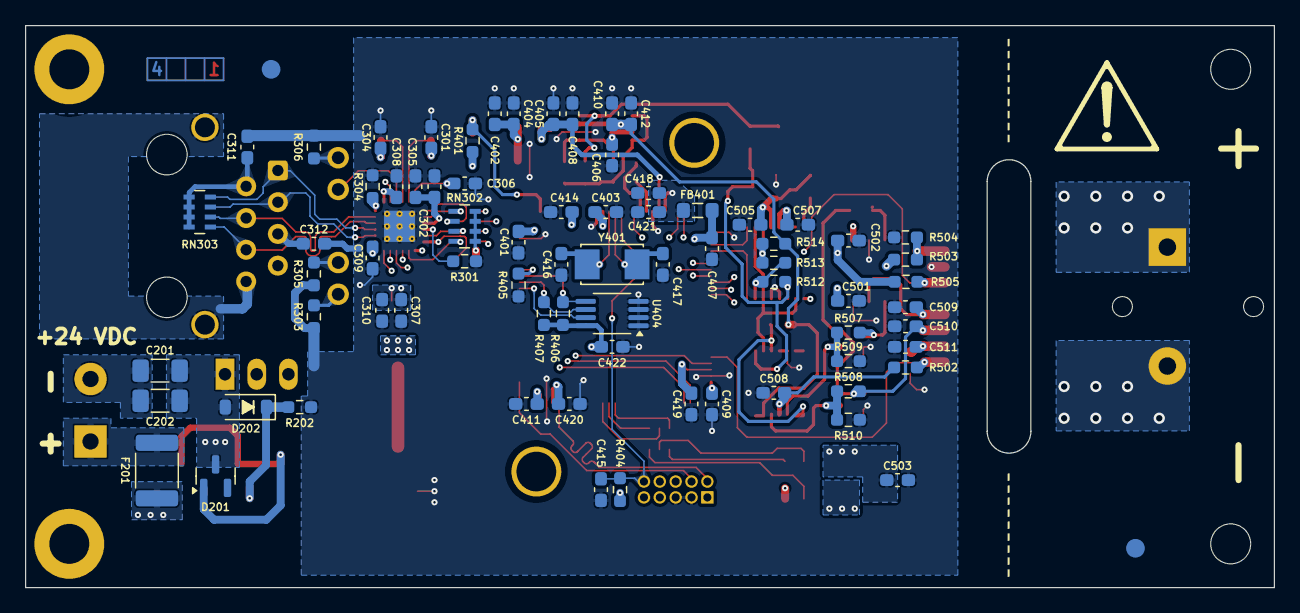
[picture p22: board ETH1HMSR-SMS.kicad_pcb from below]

Board: 4 copper layers, 100.0 x 45.0 mm, 127 parts (76 on the bottom side), 86 nets.

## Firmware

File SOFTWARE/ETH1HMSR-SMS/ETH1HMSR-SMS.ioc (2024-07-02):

#MicroXplorer Configuration settings - do not modify
ADC3.Channel-2\#ChannelRegularConversion=ADC_CHANNEL_1
ADC3.ContinuousConvMode=ENABLE
ADC3.ConversionDataManagement=ADC_CONVERSIONDATA_DMA_ONESHOT
ADC3.EOCSelection=ADC_EOC_SEQ_CONV
ADC3.EnableRegularConversion=ENABLE
ADC3.IPParameters=OversamplingMode,ConversionDataManagement,EnableRegularConversion,Rank-2\#ChannelRegularConversion,Channel-2\#ChannelRegularConversion,SamplingTime-2\#ChannelRegularConversion,OffsetNumber-2\#ChannelRegularConversion,OffsetSignedSaturation-2\#ChannelRegularConversion,NbrOfConversionFlag,ContinuousConvMode,EOCSelection,SingleDiff-2\#ChannelRegularConversion
ADC3.NbrOfConversionFlag=1
ADC3.OffsetNumber-2\#ChannelRegularConversion=ADC_OFFSET_NONE
ADC3.OffsetSignedSaturation-2\#ChannelRegularConversion=DISABLE
ADC3.OversamplingMode=DISABLE
ADC3.Rank-2\#ChannelRegularConversion=1
ADC3.SamplingTime-2\#ChannelRegularConversion=ADC_SAMPLETIME_1CYCLE_5
ADC3.SingleDiff-2\#ChannelRegularConversion=ADC_DIFFERENTIAL_ENDED
CAD.formats=
CAD.pinconfig=
CAD.provider=
CORTEX_M7.AccessPermission_S-Cortex_Memory_Protection_Unit_Region1_Settings_S=MPU_REGION_FULL_ACCESS
CORTEX_M7.AccessPermission_S-Cortex_Memory_Protection_Unit_Region2_Settings_S=MPU_REGION_FULL_ACCESS
CORTEX_M7.BaseAddress_S-Cortex_Memory_Protection_Unit_Region1_Settings_S=0x30020000
CORTEX_M7.BaseAddress_S-Cortex_Memory_Protection_Unit_Region2_Settings_S=0x30040000
CORTEX_M7.CPU_DCache=Enabled
CORTEX_M7.CPU_ICache=Enabled
CORTEX_M7.DisableExec_S-Cortex_Memory_Protection_Unit_Region1_Settings_S=MPU_INSTRUCTION_ACCESS_DISABLE
CORTEX_M7.DisableExec_S-Cortex_Memory_Protection_Unit_Region2_Settings_S=MPU_INSTRUCTION_ACCESS_DISABLE
CORTEX_M7.Enable_S-Cortex_Memory_Protection_Unit_Region1_Settings_S=MPU_REGION_ENABLE
CORTEX_M7.Enable_S-Cortex_Memory_Protection_Unit_Region2_Settings_S=MPU_REGION_ENABLE
CORTEX_M7.IPParameters=CPU_ICache,CPU_DCache,Enable_S-Cortex_Memory_Protection_Unit_Region1_Settings_S,BaseAddress_S-Cortex_Memory_Protection_Unit_Region1_Settings_S,Size_S-Cortex_Memory_Protection_Unit_Region1_Settings_S,TypeExtField_S-Cortex_Memory_Protection_Unit_Region1_Settings_S,AccessPermission_S-Cortex_Memory_Protection_Unit_Region1_Settings_S,DisableExec_S-Cortex_Memory_Protection_Unit_Region1_Settings_S,Enable_S-Cortex_Memory_Protection_Unit_Region2_Settings_S,BaseAddress_S-Cortex_Memory_Protection_Unit_Region2_Settings_S,Size_S-Cortex_Memory_Protection_Unit_Region2_Settings_S,AccessPermission_S-Cortex_Memory_Protection_Unit_Region2_Settings_S,DisableExec_S-Cortex_Memory_Protection_Unit_Region2_Settings_S,IsShareable_S-Cortex_Memory_Protection_Unit_Region2_Settings_S,IsBufferable_S-Cortex_Memory_Protection_Unit_Region2_Settings_S,default_mode_Activation
CORTEX_M7.IsBufferable_S-Cortex_Memory_Protection_Unit_Region2_Settings_S=MPU_ACCESS_BUFFERABLE
CORTEX_M7.IsShareable_S-Cortex_Memory_Protection_Unit_Region2_Settings_S=MPU_ACCESS_SHAREABLE
CORTEX_M7.Size_S-Cortex_Memory_Protection_Unit_Region1_Settings_S=MPU_REGION_SIZE_128KB
CORTEX_M7.Size_S-Cortex_Memory_Protection_Unit_Region2_Settings_S=MPU_REGION_SIZE_512B
CORTEX_M7.TypeExtField_S-Cortex_Memory_Protection_Unit_Region1_Settings_S=MPU_TEX_LEVEL1
CORTEX_M7.default_mode_Activation=1
Dma.ADC3.0.Direction=DMA_PERIPH_TO_MEMORY
Dma.ADC3.0.EventEnable=DISABLE
Dma.ADC3.0.FIFOMode=DMA_FIFOMODE_DISABLE
Dma.ADC3.0.Instance=DMA1_Stream1
Dma.ADC3.0.MemDataAlignment=DMA_MDATAALIGN_HALFWORD
Dma.ADC3.0.MemInc=DMA_MINC_ENABLE
Dma.ADC3.0.Mode=DMA_NORMAL
Dma.ADC3.0.PeriphDataAlignment=DMA_PDATAALIGN_HALFWORD
Dma.ADC3.0.PeriphInc=DMA_PINC_DISABLE
Dma.ADC3.0.Polarity=HAL_DMAMUX_REQ_GEN_RISING
Dma.ADC3.0.Priority=DMA_PRIORITY_HIGH
Dma.ADC3.0.RequestNumber=1
Dma.ADC3.0.RequestParameters=Instance,Direction,PeriphInc,MemInc,PeriphDataAlignment,MemDataAlignment,Mode,Priority,FIFOMode,SignalID,Polarity,RequestNumber,SyncSignalID,SyncPolarity,SyncEnable,EventEnable,SyncRequestNumber
Dma.ADC3.0.SignalID=NONE
Dma.ADC3.0.SyncEnable=DISABLE
Dma.ADC3.0.SyncPolarity=HAL_DMAMUX_SYNC_NO_EVENT
Dma.ADC3.0.SyncRequestNumber=1
Dma.ADC3.0.SyncSignalID=NONE
Dma.Request0=ADC3
Dma.RequestsNb=1
ETH.IPParameters=MediaInterface
ETH.MediaInterface=HAL_ETH_RMII_MODE
FREERTOS.FootprintOK=true
FREERTOS.IPParameters=Tasks01,configUSE_NEWLIB_REENTRANT,FootprintOK
FREERTOS.Tasks01=defaultTask,0,512,StartDefaultTask,Default,NULL,Static,defaultTaskBuffer,defaultTaskControlBlock
FREERTOS.configUSE_NEWLIB_REENTRANT=1
File.Version=6
GPIO.groupedBy=Group By Peripherals
I2C1.IPParameters=Timing
I2C1.Timing=0x307075B1
KeepUserPlacement=false
LWIP.BSP.number=1
LWIP.CMSIS_VERSION-Enabled=1
LWIP.DEFAULT_ACCEPTMBOX_SIZE=20
LWIP.DEFAULT_RAW_RECVMBOX_SIZE=20
LWIP.DEFAULT_TCP_RECVMBOX_SIZE=20
LWIP.DEFAULT_UDP_RECVMBOX_SIZE=20
LWIP.GATEWAY_ADDRESS=192.168.001.001
LWIP.IPParameters=LWIP_DHCP,IP_ADDRESS,NETMASK_ADDRESS,GATEWAY_ADDRESS,MEM_SIZE,LWIP_RAM_HEAP_POINTER,TCPIP_THREAD_STACKSIZE,CMSIS_VERSION-Enabled,TCP_MSS,TCP_SND_BUF,TCP_SND_QUEUELEN,MEMP_NUM_TCP_PCB_LISTEN,MEMP_NUM_NETBUF,MEMP_NUM_SELECT_CB,MEMP_NUM_TCPIP_MSG_API,MEMP_NUM_NETCONN,TCP_SYNMAXRTX,LWIP_TCP_MAX_SACK_NUM,DEFAULT_UDP_RECVMBOX_SIZE,DEFAULT_TCP_RECVMBOX_SIZE,DEFAULT_ACCEPTMBOX_SIZE,LWIP_SOCKET,MEMP_MEM_MALLOC,LWIP_IGMP,LWIP_MDNS,LWIP_MDNS_RESPONDER,MDNS_MAX_SERVICES,MDNS_RESP_USENETIF_EXTCALLBACK,MEMP_NUM_UDP_PCB,MEMP_NUM_TCP_PCB,MEMP_NUM_RAW_PCB,LWIP_RAW,LWIP_NETIF_API,DEFAULT_RAW_RECVMBOX_SIZE,LWIP_HTTPD,LWIP_NUM_NETIF_CLIENT_DATA
LWIP.IP_ADDRESS=192.168.001.017
LWIP.LWIP_DHCP=0
LWIP.LWIP_HTTPD=1
LWIP.LWIP_IGMP=1
LWIP.LWIP_MDNS=1
LWIP.LWIP_MDNS_RESPONDER=1
LWIP.LWIP_NETIF_API=1
LWIP.LWIP_NUM_NETIF_CLIENT_DATA=1
LWIP.LWIP_RAM_HEAP_POINTER=0x30020000
LWIP.LWIP_RAW=1
LWIP.LWIP_SOCKET=0
LWIP.LWIP_TCP_MAX_SACK_NUM=20
LWIP.MDNS_MAX_SERVICES=4
LWIP.MDNS_RESP_USENETIF_EXTCALLBACK=4
LWIP.MEMP_MEM_MALLOC=1
LWIP.MEMP_NUM_NETBUF=20
LWIP.MEMP_NUM_NETCONN=20
LWIP.MEMP_NUM_RAW_PCB=20
LWIP.MEMP_NUM_SELECT_CB=20
LWIP.MEMP_NUM_TCPIP_MSG_API=20
LWIP.MEMP_NUM_TCP_PCB=20
LWIP.MEMP_NUM_TCP_PCB_LISTEN=20
LWIP.MEMP_NUM_UDP_PCB=20
LWIP.MEM_SIZE=131048
LWIP.NETMASK_ADDRESS=255.255.255.000
LWIP.TCPIP_THREAD_STACKSIZE=2048
LWIP.TCP_MSS=1460
LWIP.TCP_SND_BUF=5840
LWIP.TCP_SND_QUEUELEN=16
LWIP.TCP_SYNMAXRTX=12
LWIP.Version=v2.1.2_Cube
LWIP0.BSP.STBoard=false
LWIP0.BSP.api=BSP_COMPONENT_DRIVER
LWIP0.BSP.component=LAN8742
LWIP0.BSP.condition=
LWIP0.BSP.instance=LAN8742
LWIP0.BSP.ip=
LWIP0.BSP.mode=
LWIP0.BSP.name=Driver_PHY
LWIP0.BSP.semaphore=S_LAN8742
LWIP0.BSP.solution=LAN8742
Mcu.CPN=STM32H743VIT6
Mcu.Family=STM32H7
Mcu.IP0=ADC3
Mcu.IP1=CORTEX_M7
Mcu.IP10=TIM3
Mcu.IP2=DMA
Mcu.IP3=ETH
Mcu.IP4=FREERTOS
Mcu.IP5=I2C1
Mcu.IP6=LWIP
Mcu.IP7=NVIC
Mcu.IP8=RCC
Mcu.IP9=SYS
Mcu.IPNb=11
Mcu.Name=STM32H743VITx
Mcu.Package=LQFP100
Mcu.Pin0=PE2
Mcu.Pin1=PH0-OSC_IN (PH0)
Mcu.Pin10=PA7
Mcu.Pin11=PC4
Mcu.Pin12=PC5
Mcu.Pin13=PB0
Mcu.Pin14=PB1
Mcu.Pin15=PB2
Mcu.Pin16=PB10
Mcu.Pin17=PB11
Mcu.Pin18=PB12
Mcu.Pin19=PB13
Mcu.Pin2=PH1-OSC_OUT (PH1)
Mcu.Pin20=PC6
Mcu.Pin21=PC7
Mcu.Pin22=PC8
Mcu.Pin23=PB5
Mcu.Pin24=PB6
Mcu.Pin25=PB7
Mcu.Pin26=VP_FREERTOS_VS_CMSIS_V1
Mcu.Pin27=VP_LWIP_VS_Enabled
Mcu.Pin28=VP_SYS_VS_tim1
Mcu.Pin29=VP_TIM3_VS_ClockSourceINT
Mcu.Pin3=PC1
Mcu.Pin4=PC2_C
Mcu.Pin5=PC3_C
Mcu.Pin6=PA1
Mcu.Pin7=PA2
Mcu.Pin8=PA4
Mcu.Pin9=PA5
Mcu.PinsNb=30
Mcu.ThirdPartyNb=0
Mcu.UserConstants=
Mcu.UserName=STM32H743VITx
MxCube.Version=6.11.1
MxDb.Version=DB.6.0.111
NVIC.ADC3_IRQn=true\:6\:0\:true\:false\:true\:true\:true\:true\:true
NVIC.BusFault_IRQn=true\:0\:0\:false\:false\:true\:false\:false\:false\:false
NVIC.DMA1_Stream1_IRQn=true\:5\:0\:false\:false\:true\:true\:false\:true\:true
NVIC.DebugMonitor_IRQn=true\:0\:0\:false\:false\:true\:false\:false\:false\:false
NVIC.ETH_IRQn=true\:5\:0\:false\:false\:true\:true\:true\:true\:true
NVIC.ForceEnableDMAVector=true
NVIC.HardFault_IRQn=true\:0\:0\:false\:false\:true\:false\:false\:false\:false
NVIC.MemoryManagement_IRQn=true\:0\:0\:false\:false\:true\:false\:false\:false\:false
NVIC.NonMaskableInt_IRQn=true\:0\:0\:false\:false\:true\:false\:false\:false\:false
NVIC.PendSV_IRQn=true\:15\:0\:false\:false\:false\:true\:false\:false\:false
NVIC.PriorityGroup=NVIC_PRIORITYGROUP_4
NVIC.SVCall_IRQn=true\:0\:0\:false\:false\:false\:false\:false\:false\:false
NVIC.SavedPendsvIrqHandlerGenerated=true
NVIC.SavedSvcallIrqHandlerGenerated=true
NVIC.SavedSystickIrqHandlerGenerated=true
NVIC.SysTick_IRQn=true\:15\:0\:false\:false\:false\:true\:false\:true\:false
NVIC.TIM1_UP_IRQn=true\:15\:0\:false\:false\:true\:false\:false\:true\:true
NVIC.TIM3_IRQn=true\:15\:0\:true\:false\:true\:true\:true\:true\:true
NVIC.TimeBase=TIM1_UP_IRQn
NVIC.TimeBaseIP=TIM1
NVIC.UsageFault_IRQn=true\:0\:0\:false\:false\:true\:false\:false\:false\:false
PA1.GPIOParameters=GPIO_Speed
PA1.GPIO_Speed=GPIO_SPEED_FREQ_VERY_HIGH
PA1.Mode=RMII
PA1.Signal=ETH_REF_CLK
PA2.GPIOParameters=GPIO_Speed
PA2.GPIO_Speed=GPIO_SPEED_FREQ_VERY_HIGH
PA2.Mode=RMII
PA2.Signal=ETH_MDIO
PA4.GPIOParameters=GPIO_Speed,PinState,GPIO_Label
PA4.GPIO_Label=MCU_G100
PA4.GPIO_Speed=GPIO_SPEED_FREQ_HIGH
PA4.Locked=true
PA4.PinState=GPIO_PIN_RESET
PA4.Signal=GPIO_Output
PA5.GPIOParameters=GPIO_Speed,PinState,GPIO_Label
PA5.GPIO_Label=MCU_G10
PA5.GPIO_Speed=GPIO_SPEED_FREQ_HIGH
PA5.Locked=true
PA5.PinState=GPIO_PIN_RESET
PA5.Signal=GPIO_Output
PA7.GPIOParameters=GPIO_Speed
PA7.GPIO_Speed=GPIO_SPEED_FREQ_VERY_HIGH
PA7.Mode=RMII
PA7.Signal=ETH_CRS_DV
PB0.GPIOParameters=GPIO_Label
PB0.GPIO_Label=OCD_EXT
PB0.Locked=true
PB0.Signal=GPXTI0
PB1.GPIOParameters=GPIO_Speed,GPIO_Label
PB1.GPIO_Label=MCU_ZOFFS
PB1.GPIO_Speed=GPIO_SPEED_FREQ_HIGH
PB1.Locked=true
PB1.Signal=GPIO_Output
PB10.GPIOParameters=GPIO_Label
PB10.GPIO_Label=OCD_INT
PB10.Locked=true
PB10.Signal=GPXTI10
PB11.GPIOParameters=GPIO_Speed
PB11.GPIO_Speed=GPIO_SPEED_FREQ_VERY_HIGH
PB11.Mode=RMII
PB11.Signal=ETH_TX_EN
PB12.GPIOParameters=GPIO_Speed
PB12.GPIO_Speed=GPIO_SPEED_FREQ_VERY_HIGH
PB12.Mode=RMII
PB12.Signal=ETH_TXD0
PB13.GPIOParameters=GPIO_Speed
PB13.GPIO_Speed=GPIO_SPEED_FREQ_VERY_HIGH
PB13.Mode=RMII
PB13.Signal=ETH_TXD1
PB2.GPIOParameters=GPIO_Speed,PinState,GPIO_Label
PB2.GPIO_Label=MCU_G1
PB2.GPIO_Speed=GPIO_SPEED_FREQ_HIGH
PB2.Locked=true
PB2.PinState=GPIO_PIN_SET
PB2.Signal=GPIO_Output
PB5.GPIOParameters=GPIO_Speed,PinState,GPIO_Label
PB5.GPIO_Label=EEPROM_nWP
PB5.GPIO_Speed=GPIO_SPEED_FREQ_HIGH
PB5.Locked=true
PB5.PinState=GPIO_PIN_SET
PB5.Signal=GPIO_Output
PB6.Mode=I2C
PB6.Signal=I2C1_SCL
PB7.Mode=I2C
PB7.Signal=I2C1_SDA
PC1.GPIOParameters=GPIO_Speed
PC1.GPIO_Speed=GPIO_SPEED_FREQ_LOW
PC1.Mode=RMII
PC1.Signal=ETH_MDC
PC2_C.Mode=IN1-Differential
PC2_C.Signal=ADC3_INN1
PC3_C.Mode=IN1-Differential
PC3_C.Signal=ADC3_INP1
PC4.GPIOParameters=GPIO_Speed
PC4.GPIO_Speed=GPIO_SPEED_FREQ_VERY_HIGH
PC4.Mode=RMII
PC4.Signal=ETH_RXD0
PC5.GPIOParameters=GPIO_Speed
PC5.GPIO_Speed=GPIO_SPEED_FREQ_VERY_HIGH
PC5.Mode=RMII
PC5.Signal=ETH_RXD1
PC6.GPIOParameters=PinState,GPIO_Label
PC6.GPIO_Label=LED_BLUE
PC6.Locked=true
PC6.PinState=GPIO_PIN_SET
PC6.Signal=GPIO_Output
PC7.GPIOParameters=PinState,GPIO_Label
PC7.GPIO_Label=LED_RED
PC7.Locked=true
PC7.PinState=GPIO_PIN_SET
PC7.Signal=GPIO_Output
PC8.GPIOParameters=PinState,GPIO_Label
PC8.GPIO_Label=LED_GREEN
PC8.Locked=true
PC8.PinState=GPIO_PIN_SET
PC8.Signal=GPIO_Output
PE2.GPIOParameters=GPIO_Label
PE2.GPIO_Label=MCU_DEFAULT
PE2.Locked=true
PE2.Signal=GPIO_Input
PH0-OSC_IN\ (PH0).Mode=HSE-External-Oscillator
PH0-OSC_IN\ (PH0).Signal=RCC_OSC_IN
PH1-OSC_OUT\ (PH1).Mode=HSE-External-Oscillator
PH1-OSC_OUT\ (PH1).Signal=RCC_OSC_OUT
PinOutPanel.RotationAngle=0
ProjectManager.AskForMigrate=true
ProjectManager.BackupPrevious=false
ProjectManager.CompilerOptimize=6
ProjectManager.ComputerToolchain=false
ProjectManager.CoupleFile=false
ProjectManager.CustomerFirmwarePackage=
ProjectManager.DefaultFWLocation=true
ProjectManager.DeletePrevious=true
ProjectManager.DeviceId=STM32H743VITx
ProjectManager.FirmwarePackage=STM32Cube FW_H7 V1.11.2
ProjectManager.FreePins=false
ProjectManager.HalAssertFull=false
ProjectManager.HeapSize=0x200
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

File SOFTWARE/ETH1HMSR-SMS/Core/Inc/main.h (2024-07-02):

/* USER CODE BEGIN Header */
/**
  ******************************************************************************
  * @file           : main.h
  * @brief          : Header for main.c file.
  *                   This file contains the common defines of the application.
  ******************************************************************************
  * @attention
  *
  * Copyright (c) 2024 STMicroelectronics.
  * All rights reserved.
  *
  * This software is licensed under terms that can be found in the LICENSE file
  * in the root directory of this software component.
  * If no LICENSE file comes with this software, it is provided AS-IS.
  *
  ******************************************************************************
  */
/* USER CODE END Header */

/* Define to prevent recursive inclusion -------------------------------------*/
#ifndef __MAIN_H
#define __MAIN_H

#ifdef __cplusplus
extern "C" {
#endif

/* Includes ------------------------------------------------------------------*/
#include "stm32h7xx_hal.h"

#include "stm32h7xx_ll_rcc.h"
#include "stm32h7xx_ll_crs.h"
#include "stm32h7xx_ll_bus.h"
#include "stm32h7xx_ll_system.h"
#include "stm32h7xx_ll_exti.h"
#include "stm32h7xx_ll_cortex.h"
#include "stm32h7xx_ll_utils.h"
#include "stm32h7xx_ll_pwr.h"
#include "stm32h7xx_ll_dma.h"
#include "stm32h7xx_ll_gpio.h"

/* Private includes ----------------------------------------------------------*/
/* USER CODE BEGIN Includes */

/* USER CODE END Includes */

/* Exported types ------------------------------------------------------------*/
/* USER CODE BEGIN ET */

/* USER CODE END ET */

/* Exported constants --------------------------------------------------------*/
/* USER CODE BEGIN EC */

/* USER CODE END EC */

/* Exported macro ------------------------------------------------------------*/
/* USER CODE BEGIN EM */

/* USER CODE END EM */

/* Exported functions prototypes ---------------------------------------------*/
void Error_Handler(void);

/* USER CODE BEGIN EFP */

/* USER CODE END EFP */

/* Private defines -----------------------------------------------------------*/
#define MCU_DEFAULT_Pin LL_GPIO_PIN_2
#define MCU_DEFAULT_GPIO_Port GPIOE
#define MCU_G100_Pin LL_GPIO_PIN_4
#define MCU_G100_GPIO_Port GPIOA
#define MCU_G10_Pin LL_GPIO_PIN_5
#define MCU_G10_GPIO_Port GPIOA
#define OCD_EXT_Pin LL_GPIO_PIN_0
#define OCD_EXT_GPIO_Port GPIOB
#define MCU_ZOFFS_Pin LL_GPIO_PIN_1
#define MCU_ZOFFS_GPIO_Port GPIOB
#define MCU_G1_Pin LL_GPIO_PIN_2
#define MCU_G1_GPIO_Port GPIOB
#define OCD_INT_Pin LL_GPIO_PIN_10
#define OCD_INT_GPIO_Port GPIOB
#define LED_BLUE_Pin LL_GPIO_PIN_6
#define LED_BLUE_GPIO_Port GPIOC
#define LED_RED_Pin LL_GPIO_PIN_7
#define LED_RED_GPIO_Port GPIOC
#define LED_GREEN_Pin LL_GPIO_PIN_8
#define LED_GREEN_GPIO_Port GPIOC
#define EEPROM_nWP_Pin LL_GPIO_PIN_5
#define EEPROM_nWP_GPIO_Port GPIOB

/* USER CODE BEGIN Private defines */

/* USER CODE END Private defines */

#ifdef __cplusplus
}
#endif

#endif /* __MAIN_H */

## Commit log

2024-07-12 BOM updated
    [Current.kicad_sch, ETH1HMSR-SMS-B_Cu.gbr, ETH1HMSR-SMS-B_Mask.gbr, ETH1HMSR-SMS-B_Paste.gbr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]
2024-08-14 Small improvements.
    [ETH1HMSR-SMS.kicad_pcb]
2024-11-14 service.html : bug fix in nominal current selection.
